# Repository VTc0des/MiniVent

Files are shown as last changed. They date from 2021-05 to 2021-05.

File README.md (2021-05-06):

# MiniVent Platform IO Build

### Rice University - Global Medical Innovation & Oshman Engineering Design Kitchen

###### Authors: Varsha Thomas, Thomas Herring

This repository contains all the working code for the MAIN, follower1 (F1), and follower2 (F2) Arduino UNO microcontrollers to build the MiniVent device, a low-cost pediatric bridge ventilator. Feel free to fork it for your own development, we encourage collaboration! All mechanical parts and assembly instructions to build the predicate device (ApolloBVM - the adult bridge ventilator) can be found [here](http://oedk.rice.edu/apollobvm), a bill of materials, and a slide deck can be found in the google drive supplied by the 2020-2021 BIOE 530 Design Team

## System Overview

The MiniVent system uses three coordinated microcontrollers in order to facilitate user input while guaranteeing uninterrupted airflow to the patient. The system has a MAIN controller, responsible for managing the display and user input for the control panel, the F1 controller that actually sends motor commands to the servos, and an F2 controller that interfaces with the patient monitoring system which is comprised of a pressure sensor, and RGB LCD display to display patient parameters to the screen. 

The MAIN controller operates separately from both F1 and F2 and ensures that the system is real-time safe. In order to give more clarity about the technical operation of this device, we will outline the operation of each controller separately.

In order to facilitate the various functions of the device, F1 controller operates in 5 distinct states: load, on, off, and 2 states for an inspiratory hold maneuver. While in the ‘load’ state, F1 controller will read ventilation parameters from MAIN over the I2C bus, generate a new trajectory with these parameters, and turn its state to ‘on’. While in the ‘on’ state, the device will follow the trajectory over and over for infinity. This means that the F1 controller will never stop moving the motors unless it receives a command from MAIN to change its state to ‘stop’. If the master controller were to do so, the device would finish its current cycle and stop moving. In the first state for the inspiratory hold maneuver, F1 will generate a new trajectory that pauses the motors at the setpoint for 0.5 seconds, changes state to implement the inspiratory hold trajectory which it will follow for one cycle then reload the previous trajectory. 

The MAIN controller is mainly tasked with running the user display and sending commands to F1. Internally, MAIN switches which panel is currently displaying and manages input from the encoder and buttons. Each panel that the master displays is programmed to follow a different behavior and is modular. This makes it easy to implement panels that behave completely differently and interact with the F1 controller on the fly.

The F2 controller is the primary system for running the alarm display, sending and recieving commands to/from F1 for implementing an inspiratory hold maneuver, and reading and processing input from external sensors. In the current iteration of the device, F2 interfaces with a gauge pressure sensor. Internally, F2 manages input from the inspiratory hold button, reads pressure sensor data, manages output to the patient LED alarms, and displays patient respiration information to the user. 

## Installation Instructions

1. Install PlatformIO using the instructions [here](https://platformio.org/install).
   1. On Linux, run `pip3 install -U platformio` to install PlatformIO.
2. Clone this repository onto your local machine.
   1. On Linux, run `git clone https://github.com/apollobvm/apollobvm_pio.git` to clone the repo.
3. Build the PlatformIO project with either the core toolchain or IDE plugins.
   1. On Linux, run `pio run` to build.
4. Choose which environment to upload - `main`, `f1`, and `f2`, and specify with the `-e` flag.
   1. On Linux, run `pio run -e desired_env -t upload` to upload.

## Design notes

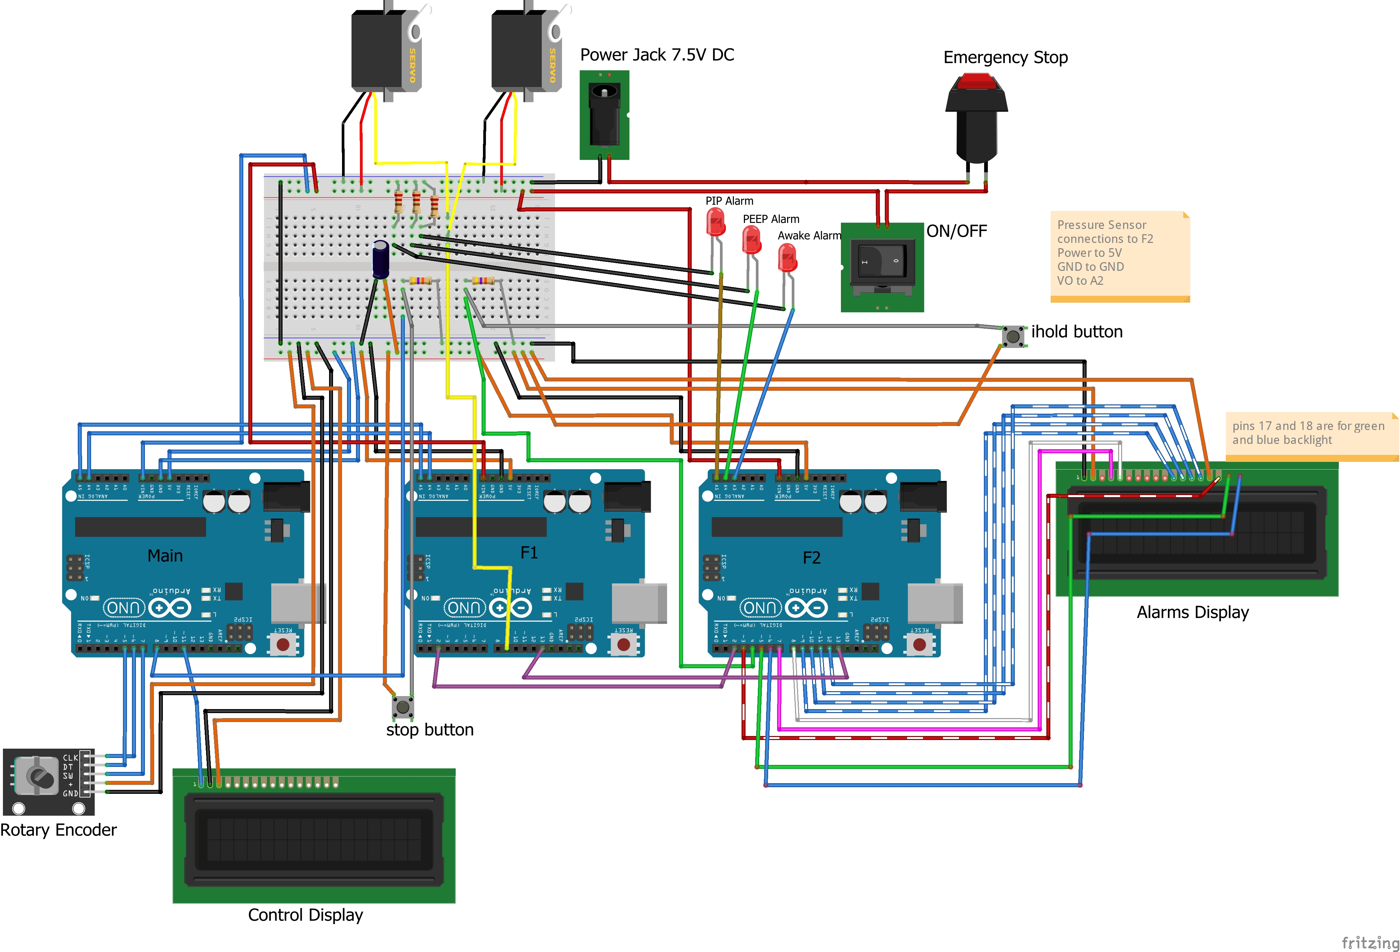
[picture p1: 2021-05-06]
Breadboard Circuit.jpg

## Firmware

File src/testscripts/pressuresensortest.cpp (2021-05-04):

#ifdef PST

/*Credit for the filtering algorithm:
 * https://www.norwegiancreations.com/2016/03/arduino-tutorial-simple-high-pass-band-pass-and-band-stop-filtering/
 */

#include <Arduino.h>
#include <LiquidCrystal.h>
#include <Wire.h>

#define REDLITE 3
#define GREENLITE 5
#define BLUELITE 6

#define AWAKE_ALARM A3
#define PEEP_ALARM A4
#define PIP_ALARM A5

#define PS_PIN A2
#define SAMPLE_RATE 20    //sampling rate of 20 ms
#define SAMPLE_SIZE 100

#define F2_TO_F1 2
#define F1_TO_F2 13

// initialize the library with the numbers of the interface pins
LiquidCrystal lcd(7, 8, 9, 10, 11, 12);

// you can change the overall brightness by range 0 -> 255
const uint8_t brightness = 255;

const uint8_t led_on = 255;
const uint8_t led_off = 0;

const float mBar_cmH2O = 1.01972;

uint8_t i;

int readPressure;
int savePressure[SAMPLE_SIZE];

float EMA_a_low = 0.7; //initialization of EMA alpha
int EMA_S_low = 0; //initialization of EMA S

unsigned long currentRead;
unsigned long previousRead;
double baseline;

float pip;
float peep;
float pp;
float max_pip = 35; //35 cmH2O
//const String display_lines[3] = {"PIP = ", "PEEP = ", "PP = "};

void printWarning();
void startDisplay();
void read_filter();
void calculatePIP();
void displayPIP();
void setBacklight(uint8_t r, uint8_t g, uint8_t b);

void setup()
{
  Serial.begin(9600); //baudrate 9600

  lcd.begin(20, 4);

  // Congifure pinMode for communicating F2 <-> F1;
  pinMode(F2_TO_F1, OUTPUT);
  pinMode(F1_TO_F2, INPUT);

  printWarning();
  startDisplay();

  //initialize variables
  pip = 0;
  peep = 0;
  pp = 0;
  i = 0;

  baseline = analogRead(PS_PIN); // obtains first value once start up
  // baseline = (baseline * 100 * mBar_cmH2O) / 1023;
  //filter raw data
//  EMA_S_low = ((EMA_a_low * baseline) + ((1 - EMA_a_low) * EMA_S_low)); //run the EMA

  EMA_S_low = baseline; //set EMA_S_low for t=0

  previousRead = millis();
}

void loop()
{
  read_filter();

  //if all samples have been collected, reset counter, process and display
  if (i == SAMPLE_SIZE)
  {
    i = 0; //reset i to 0.
    Serial.println("CALCULATING");
    calculatePIP();
    displayPIP();
  }
}

void printWarning() {
  setBacklight(0, 128, 128);
  lcd.setCursor(6, 1);
  lcd.print("MINIVENT");
  delay(2000);
  lcd.clear();
  lcd.setCursor(6, 1);
  lcd.print("WARNING");
  lcd.setCursor(1, 2);
  lcd.print("USE PEDI SIZED BAG");
  delay(2000);
  lcd.clear();
}

void startDisplay() {
  setBacklight(0, 128, 128);
  lcd.setCursor(0, 1);
  lcd.print("PIP = ");
  lcd.setCursor(0, 2);
  lcd.print("PEEP = ");
  lcd.setCursor(0, 3);
  lcd.print("PP = ");
}

void read_filter() {
  //sample pressure
  currentRead = millis();
  if (currentRead - previousRead > SAMPLE_RATE)
  {
    previousRead = currentRead;
    readPressure = (analogRead(PS_PIN));

    //filter raw data
    EMA_S_low = ((EMA_a_low * readPressure) + ((1 - EMA_a_low) * EMA_S_low)); //run the EMA

    savePressure[i] = EMA_S_low;

//    Serial.print("Baseline:");
//    Serial.print(baseline);
//    Serial.print(" ");
//    Serial.print("Pressure:");
    Serial.print("Pressure,");
    Serial.println(savePressure[i]);

    //increment counter
    i++;
  }
}

void calculatePIP() {
  int maxValue = savePressure[0]; //save first value in array
  for (uint8_t j = 0; j < SAMPLE_SIZE; j++) {
    if (savePressure[j] > maxValue) {
      maxValue = savePressure[j];
    }
  }

  //  Serial.print("Max Value");
  //  Serial.println(maxValue);
  //  Serial.print("ADC PIP Value ");
  //  Serial.println((maxValue - baseline));
  Serial.print("mx value,");
  Serial.println(maxValue - baseline);
  //convert to voltage output, then to mBar, then to cmH2O
  pip = ((maxValue - baseline) * 100 * mBar_cmH2O) / 1023;
//  pip = (maxValue * 100 * mBar_cmH2O) / 1023;
  

//    Serial.print("PIP");
//    Serial.println(pip);
}

void displayPIP() {
  if (pip > max_pip) {
    //print to first line
//    lcd.setCursor(0, 0);
//    lcd.print("ALERT: HIGH IP");
    setBacklight(255, 0, 0);
    analogWrite(PIP_ALARM, led_on);
  }
//  else if (pip < baseline) {
//    //print to first line
////    lcd.setCursor(0, 0);
////    lcd.print("ALERT: AWAKE");
//    setBacklight(255, 0, 0);
//    analogWrite(AWAKE_ALARM, led_on);
//  }
  else {
    lcd.setCursor(4, 0);
    lcd.print("VENTILATING");
//    lcd.print("BASE = ");
//    lcd.setCursor(8, 0);
//    lcd.print(baseline);
    setBacklight(0, 255, 0);
    analogWrite(PIP_ALARM, led_off);
    analogWrite(AWAKE_ALARM, led_off);
  }

  lcd.setCursor(8, 1);
  lcd.print(pip);
  lcd.setCursor(8, 2);
  lcd.print(peep);
  lcd.setCursor(8, 3);
  lcd.print(pp);
}

void setBacklight(uint8_t r, uint8_t g, uint8_t b) {
  // normalize the red LED - its brighter than the rest!
  // r = map(r, 0, 255, 0, 100);
  // g = map(g, 0, 255, 0, 150);

  r = map(r, 0, 255, 0, 255);
  g = map(g, 0, 255, 0, 255);

  r = map(r, 0, 255, 0, brightness);
  g = map(g, 0, 255, 0, brightness);
  b = map(b, 0, 255, 0, brightness);

  // common anode so invert!
  r = map(r, 0, 255, 255, 0);
  g = map(g, 0, 255, 255, 0);
  b = map(b, 0, 255, 255, 0);
  //  Serial.print("R = "); Serial.print(r, DEC);
  //  Serial.print(" G = "); Serial.print(g, DEC);
  //  Serial.print(" B = "); Serial.println(b, DEC);
  analogWrite(REDLITE, r);
  analogWrite(GREENLITE, g);
  analogWrite(BLUELITE, b);
}

#endif

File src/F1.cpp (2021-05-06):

#ifdef MOT

#include <Wire.h>
#include <Servo.h>
#include <trajfactory.h>
#include "constants.h"
#include "pins.h"

// Address of slave.
#define SLAVE_ADDR 8

// Pin definitions.
#define SERVO_PIN 9

// Limits of servo.
#define SERVO_MIN 2400
#define SERVO_MAX 550

// Init trajectory generation and current pointer.
TrajFactory tf = TrajFactory();
Trajectory* traj_ptr = 0;

// Init servo class.
Servo servo;

// Init current ventilator params.
int rr;
float ie;
int setpoint;
float hold;
int delta_t;
char state;

// Init I-Hold params
bool iholdComplete;
bool iholdStart;
int currIHoldStep;
unsigned long startIHoldTime;

void moveTo(int pos, int delta_t){

  // Write current position instruction to console.
  Serial.print("Position:");
  Serial.println(pos);

  // Move the servos to next setpoint 
  servo.writeMicroseconds(SERVO_MIN-pos);

  // Wait delta time.
  delay(delta_t);
}

void stop(){

  // If we have already generated a trajectory, follow it till the end.
  if (traj_ptr != 0) {
    while (traj_ptr->getCurrentStep() != 0) {
      moveTo(traj_ptr->nextStep(), traj_ptr->getDeltaTime());
    }
  // If not, got to 0 position.
  } else {
    moveTo(0, 100);
  }
}

void recieveTraj(int num_entries) {

  // Read the state from incoming transmission.
  char recieved_state = Wire.read();

  // Either change machine state or load new settings.
  switch (recieved_state) {
    case 'X':
      state = 'X';
      break;
    case 'L':
      if (state !='I') {
        state = 'L';
      }
      
      // Load new params
      byte high = Wire.read();
      byte low = Wire.read();
      setpoint = (high << 8) | low;

      rr = Wire.read();

      byte inhale = Wire.read();
      byte exhale = Wire.read();
      ie = float(inhale) / exhale;

      byte hold_s = Wire.read();
      byte hold_dec = Wire.read();
      hold = hold_s + hold_dec/100.0;

      delta_t = Wire.read();

      break;
  }
}

void setup() {

  // Join i2c bus with address SLAVE_ADDR.
  Wire.begin(SLAVE_ADDR);

  // Register callback function for i2c receive.
  Wire.onReceive(recieveTraj);

  // Start serial output for trajectory monitoring.
  Serial.begin(9600);

  // Attach servo.
  servo.attach(SERVO_PIN);

  // Initialize I-Hold parameters
  iholdComplete = false;
  iholdStart = true;  //set to true in setup so first ihold will run. 

  /// Congifure pinMode for communicating F1 <-> F2;
  pinMode(F2_TO_F1, INPUT);
  pinMode(F1_TO_F2, OUTPUT);

  // Set state to off.
  state = 'X';
}

void loop() {
  if (digitalRead(F2_TO_F1) == HIGH && state != 'I' && state != 'C' && state != 'L' && state != 'X') {
    // if signal recieved from F2 AND not already in C, I, L, or X states (confirm, initiate, load, stop)
    // set the state to C to confirm ihold
    state = 'C';  
  } 

  // Run device in different modes.
  switch (state) {

    // Device is on, continue following trajectory.
    case 'O': 
      moveTo(traj_ptr->nextStep(), traj_ptr->getDeltaTime());
      break;

    // Device has been instructed to shutdown.
    case 'X':
      stop();
      break;

    // Device has recieved a new trajectory, load and start.
    case 'L':

      // Stop motion.
      stop();

      // If assigned ptr, delete contents
      if (traj_ptr != 0) {
        delete traj_ptr;
      }

      // Build new trajectory
      traj_ptr = tf.build(rr, ie, setpoint, hold, delta_t);

      // Set device on.
      state = 'O';
      break;

    // Device has recieved confirm ihold state, load ihold trajectory then start
    case 'C':

      // Stop motion.
      stop();

      if (traj_ptr != 0){
        delete traj_ptr;
      }
      
      // Build new trajectory
      traj_ptr = tf.build(rr, ie, setpoint, IHOLD_TIME, delta_t);

      // Set device on.
      state = 'I';
      break;

       // Device has been instructed to maintain inspiratory hold manuever
    case 'I':

      currIHoldStep = traj_ptr->nextStep();
      moveTo(currIHoldStep, traj_ptr->getDeltaTime());

      // Send signal to F2 that ihold initiated.
      if (currIHoldStep == setpoint) {
        digitalWrite(F1_TO_F2, HIGH);
        
        //start time only when currIHoldStep reaches the setpoint. 
        if (iholdStart){
          Serial.println("Begin I-HOLD");
          // Start clock on IHold
          startIHoldTime = millis();
          iholdStart = false;
        } //end of if
        
        // Check if 0.5s have passed
        if (millis() - startIHoldTime >= IHOLD_TIME*1000) {
          iholdComplete = true;
          iholdStart = true;  //reset the variable for the next ihold implementation
        } //end of if
      } 
      else {
        digitalWrite(F1_TO_F2, LOW);
        if (iholdComplete){
          Serial.println("End I-HOLD");
          iholdComplete = false;  //reset the variable for the next ihold implementation
          state = 'L';
        }
      }
      break;
  } //end of switch
} //end of loop

#endif

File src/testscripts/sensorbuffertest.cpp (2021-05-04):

#ifdef SBTST
#include "sensorbuffer.h" //include alarmdisplay.h and alarmproperties.h separetly to avoid cyclic inclusion of libraries.
#include <Arduino.h>
#include <Wire.h>

#define PS_PIN A2

const uint8_t _sample_rate = 20;   //poll for a new pressure sample every 20 ms
const float _EMA_a_low = 0.7;      //initialization of EMA alpha
const uint8_t _bufferLength = 100;

//variables to hold baseline and current reading
int _baseline = 0;
int _pressureReading = 0;

int _EMA_S_low = 0; //initialization of EMA S

//variables to track time
unsigned long _currentRead;
unsigned long _previousRead;
//pin location for the pressure sensor.
uint8_t _pressure_pin = PS_PIN;

SensorBuffer sb(_bufferLength);

void setup() {
  Serial.begin(9600);

  for (uint16_t i = 0; i < _bufferLength; i++) {
    sb.putBack(0);
  }

  Serial.println("Populated SensorBuffer...");
  Serial.println("Printing contents of SensorBuffer..");
  _EMA_S_low = analogRead(_pressure_pin);
  _baseline = _EMA_S_low;
  _previousRead = millis();
}

void loop() {

  for (uint16_t i = 0; i < _bufferLength; i++) {
    Serial.print("i: ");
    Serial.print(i);
    Serial.print(" sb: ");
    Serial.println(sb.get(i));
  }

    // Add another break.
  Serial.println();
  _currentRead = millis();
    if (_currentRead - _previousRead > _sample_rate) {
        _previousRead = _currentRead;
        _pressureReading = analogRead(_pressure_pin);

        //filter raw data
        _EMA_S_low = ((_EMA_a_low * _pressureReading) + ((1 - _EMA_a_low) * _EMA_S_low)); //run the EMA

        //put it into the array
        sb.putBack(_EMA_S_low);

        //check if current val > previous val
        if (sb.get(_bufferLength-1) > sb.get(_bufferLength-2)) {
          Serial.println("increasing");
        }
        else if (sb.get(_bufferLength-1) < sb.get(_bufferLength-2)) {
          Serial.println("decreasing");
        }
        else {
          Serial.println("no change");
        }
    }
}

#endif

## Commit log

2021-04-20 Fixed bugs in SensorBuffer
2021-04-22 add ihold duration-stuck in while, pressure filter
2021-04-29 added pressure manager; tested adisplaytest.cpp;
2021-05-03 added sensor buffer init code to calibrate
2021-05-04 implemented plateau pressure calculation in PM.cpp
2021-05-04 physical circuit has two breadboards
2021-05-04 Fritzing Schematic for Circuit
    [Circuit.fzz]
2021-05-04 updated to include information about MiniVent device
2021-05-06 change float to doubles for pressure vars for disp
